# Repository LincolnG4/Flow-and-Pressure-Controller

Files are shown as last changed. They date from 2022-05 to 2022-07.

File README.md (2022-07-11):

# Protótipo de controle de fluxo de massa e leitura de pressão



O objetivo principal deste trabalho é desenvolver um protótipo de um sistema, composto de _hardware_, _firmware_ e _software_, para controle do fluxo e pressão de gases durante tratamento de materiais.

Os objetivos :

- Desenvolver um protótipo de um sistema de controle e alimentação de 4 _MFC_ MKS 500 _SCCM_ e leitura de pressão através de 1 Pirani APGX-M-NW16/ALI Edwards;

-  Desenvolver modos de funcionamento programados, tais como: liga/desliga de coleta sensores, pre-sets de gases comuns e alerta de erro;
- Desenvolver a placa de circuito impresso;
- Desenvolver a coleta de dados dos sensores.

## Wish list
Lista de desejos para o futuro do projeto:  
- [ ] Estudo mais detalhado dos resultados dos sinais aplicando metrologia; _`Em desenvolvimento`_
- [ ]  Sofware em Python para concatenar e gerar um grafico interativo; _`Em desenvolvimento`_
- [ ] Utilização de um hardware com Wi-Fi embutido e com mais de um núcleo, assim, permitindo multitarefas;
- [ ] Utilização de um processador de fácil integração na placa PCB;
- [ ] Otimização da programação; _`Em desenvolvimento`_
- [ ] Garantir a não utilização de um hardware genérico;
- [ ] Utilização de um roteador de internet dentro do laboratório;
- [ ] Remodelar o case para montagem por encaixe clicáveis ao invés de parafusos; _`Em desenvolvimento`_
- [ ] Função para alteração de data e hora do RTC; _`Em desenvolvimento`_

# 1. Visão Geral

 - Fonte de alimentação: 24 V ( **O módulo Step-Down aceita até 40 V de entrada, porém é necessário desmonta-lo e regular através do parafuso a saída para 7V** )
 - Sinal de saída: 0-5 V
 - Dimensões: 165,5 x 74,6 x 41 mm
 - Tela: Nextion Touch 320x240
 - Armazenamento: cartão microSD até 64 GB e 15GB em nuvem
 - Portas: 4 entradas DB9-macho, 1 entrada RJ45-femea e uma porta usb (debug)

## 1.1 Componentes

| Componente | Unidade | Preço/unidade (R$) | Total | Link | 
|--|--|--|--|--|
|Arduino Mega|1| 200,00 | 200,00  | [Compre](https://www.baudaeletronica.com.br/arduino-mega-2560-compativel-cabo-usb.html) |
| Capacitor 1uF |9| 0,23 | 2,07 | [Compre](https://www.eletrogate.com/capacitor-eletrolitico-1uf-x-50v ) |
| Conector DB9|4|3,00  | 12,00 |  [Compre](https://www.soldafria.com.br/conector-db9-macho-90-graus-solda-placa-p-1709.html) |
| Conector RJ45 |1|4,00 | 4,00  |  |
| Conector Alimentação|1| 2,50 | 2,50  | [Compre](https://www.robocore.net/conector/conector-dc-p4-femea)  |
| Fonte de alimentação 24V |1| 30,00 | 30,00 |  |
| Modulo Leitor de microSD | 1 | 12,00 | 12,00 | [Compre](https://www.eletrogate.com/modulo-micro-sd-card)  |
| Modulo LM2596 StepDown | 1 |15,00  | 15,00  | [Compre](https://www.filipeflop.com/produto/regulador-de-tensao-lm2596-conversor-dc-dc-step-down/) |
| Modulo WiFi ESP8266 |1| 20,00 | 20,00  | [Compre](https://www.eletrogate.com/modulo-wifi-serial-esp8266-esp-01) |
| Resistor 4.7k Ohms |6|0,05| 0,30 | [Compre](https://www.eletrogate.com/resistor-4k7-1-4w-10-unidades ) |
| Resistor 470 Ohms |8| 0,05 |0,40 |[Compre](https://www.eletrogate.com/resistor-4k7-1-4w-10-unidades )  |
| Resistor 220 Ohms |1| 0,05 | 0,05  |[Compre](https://www.eletrogate.com/resistor-4k7-1-4w-10-unidades ) |
| RTC 1302 | 1 | 10,00 |10,00 | [Compre](https://www.eletrogate.com/modulo-real-time-clock-ds1302) |
| Tela Nextion 320x240 |1| 120,00 |120,00  | [Compre](https://pt.aliexpress.com/item/32685352949.html?spm=a2g0o.productlist.0.0.10a12308w7t6Pf&algo_pvid=ee404ca7-f5a8-4c20-a123-40767543fb84&algo_exp_id=ee404ca7-f5a8-4c20-a123-40767543fb84-0&pdp_ext_f=%7B%22sku_id%22%3A%2260390805771%22%7D&pdp_npi=2%40dis%21BRL%21%21102.36%21%21%2133.26%21%21%402101d4a716547459631704164eff88%2160390805771%21sea)|
| Transistor BC337 |4| 0,27 | 1,08 | [Compre](https://www.eletrogate.com/ecfjb2rzm-transistor-npn-bc337)  |
| __TOTAL__ ||  |  __544,40__|  |

## 1.2 Tabela de fatores de correção dos gases

Faça o download da tabela de fatores de coreção dos gases em  [DOWNLOAD](https://github.com/LincolnG4/Flow-and-Pressure-Controller/blob/main/gasfactor.xlsx)

## 1.3 FAQ & Troubleshooting

> **A tela do produto está funcionando mas ele não retorna nenhum valor de medição**

- Certifique-se que os conectores da tela estão soldados corretamente 
- Conecte o Arduino na porta USB do seu computador e siga os passos  do tópico `3.3.1.1`
- Certifique-se que não aparecerá nenhuma mensagem de erro no monitor

# 2. Software Utilizados

| SOFTWARE        | DESCRIÇÃO|DOWNLOAD |
|----------------|-------------------------------|-------------------------------|
|`Cura3D`|Software para impressão 3D|https://ultimaker.com/software/ultimaker-cura|
|`FreeCAD 0.19`|CAD|https://www.freecadweb.org/downloads.php	|
|`Kicad 6.0`|Eletrônica e PCB |https://www.kicad.org/download/|
|`Nextion Editor`|Edição da interface LCD|https://nextion.tech/nextion-editor/|
|`Photopea`|Edição de fotos|https://photopea.com/|
|`Schematic editor`|Auto routing para trilha PCB|https://layouteditor.com/download|
|`Visual Studio Code e/ou Arduino IDE`|Edição de codigos|https://code.visualstudio.com / https://www.arduino.cc/en/software/download|

## 2.2 Links úteis 
[Basico do Arduino](https://www.if.ufrj.br/~gpenello/DisciplinasAntigas/Lab2_2018-1/GUIA_ARDUINO_v.2.pdf)
[Básico de Linguagem C++](https://www.inf.ufpr.br/ci208/NotasAula.pdf)
[Básico Cura 3D](https://3dlab.com.br/cura-3d-ultimaker/)
[FreeCAD -> SolidWorks / SolidWorks -> FreeCAD](https://forum.freecadweb.org/viewtopic.php?style=4&t=20778)

# 3. Passo a Passo de construção e instalação
## 3.1 Impressão do  case 3D

Faça o download dos arquivos para impressão 3D:
- [Gabinete](https://github.com/LincolnG4/Flow-and-Pressure-Controller/blob/main/Hardware/CAD/case_bottom-Body.stl)
- [Tampa](https://github.com/LincolnG4/Flow-and-Pressure-Controller/blob/main/Hardware/CAD/case_top-Body.stl)

Recomendações:

- Materiais: PLA ou ABS;
- Confira a [tabela de temperatura](https://3dlab.com.br/temperatura-na-impressao-3d/) para o bico para cada material;
- Configuração através do software [Cura 3D](#software-utilizados):  

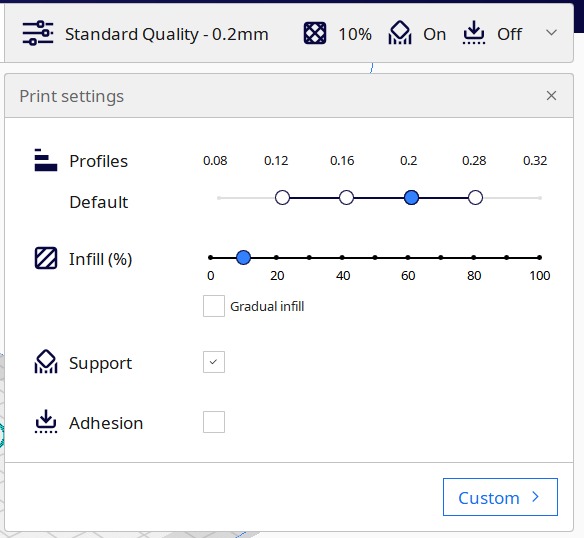
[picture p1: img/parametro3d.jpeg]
parameters


## 3.2 Configurando seu ambiente de programação
 Faça o download das bibliotecas a seguir e siga o passo a passo para configuração do seu ambiente de desenvolvimento.
 
### 3.2.1 Bibliotecas Externas Utilizadas 

#### Arduino 

Versão da placa: Arduino AVR Boards 1.8.3
| SOFTWARE        | DESCRIÇÃO|DOWNLOAD |
|----------------|-------------------------------|-------------------------------|
|`ITEADLIB Arduino`|Auxiliar no controle da tela LCD|https://github.com/itead/ITEADLIB_Arduino_Nextion|
|`ArduinoRTClibrary`|Controle do modulo RTC|https://github.com/chrisfryer78/ArduinoRTClibrary|
|`Timelib`|Manipulação time string|https://github.com/PaulStoffregen/Time|
|`UnixTime`|Manipulação de timestamp|https://github.com/GyverLibs/UnixTime|
_______

#### ESP01 

Versão da placa: esp8266 2.4.3
| SOFTWARE        | DESCRIÇÃO|DOWNLOAD |
|----------------|-------------------------------|-------------------------------|
|`WiFi Manager`|Auxiliar no controle do WiFi|https://github.com/tzapu/WiFiManager|

### 3.2.2 Como instalar uma biblioteca 

 1. Abra o link para o donwload da biblioteca (ex: `https://github.com/itead/ITEADLIB_Arduino_Nextion`) e faça o download do `.ZIP`  
download 
2. Abra o `Arduino IDE` e vá em `Sketch`>`Incluir biblioteca`> `Adicionar biblioteca .ZIP`  
include
3. Selecione a biblioteca que você fez o download no Passo 1 

### 3.2.3 Como instalar os gerenciador de placa 

#### Arduino 

1. Abra o `Arduino IDE` e clique em `Ferramentas`>`Placa`>`Gerenciador de placas`  

Como programar o NodeMCU com Arduino IDE   
2. Procure pela placa `Arduino AVR Boards` e selecione a versão `1.8.3`  
_______
#### ESP01
1.Abra o `Arduino IDE` e vá em `Arquivos`>`Preferências`  
2. No campo `URLs adicionais de Gerenciadores de Placas`, insira o link  `http://arduino.esp8266.com/stable/package_esp8266com_index.json`  

Como programar o NodeMCU com Arduino IDE
3. Vá em `Ferramentas`>`Placa`>`Gerenciador de placas`  
4. Procure pela placa `esp8266 by ESP8266 community` e selecione a versão `2.4.3`  
 
## 3.3  Implementando firmware
Com todas as bibliotecas configuradas, é possível desenvolver e carregar o código para o  Arduino, Esp e Nextion.

`Faça o download desse respositório e descompacte em alguma pasta do seu computado`:
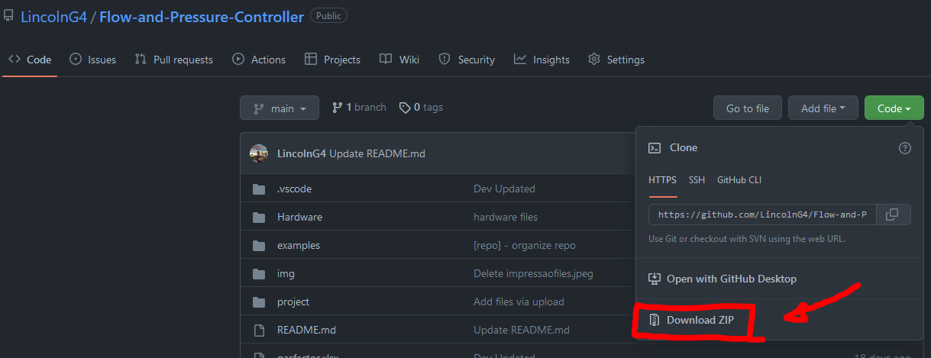
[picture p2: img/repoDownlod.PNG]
Download repositorio


### 3.3.1 Arduino
- Abra o [`Arduino IDE`](https://github.com/LincolnG4/Flow-and-Pressure-Controller/blob/main/README.md#2Software-Utilizados) em seu computador e vá em `Arquivo` > `Abrir`
- Vá até a pasta onde voce descompactou o repositório repositório, navegue por `Flow-and-Pressure-Controller-main` > `project` > `main.ino`   
- Certifique-se que a pasta `lib` esta na mesma pasta que o `main.lib`  
ConfMain
- Conecte o `Arduino Mega` via porta `USB`  
- Clique em `Ferramentas` e selecione as configurações :  
  
 *obs: a porta irá variar de acordo com a porta que o Arduino foi conectado ao seu dispositivo 

- Clique no botão `Verificar`, se o IDE não retornar nenhum erro, clique no botão `Carregar`
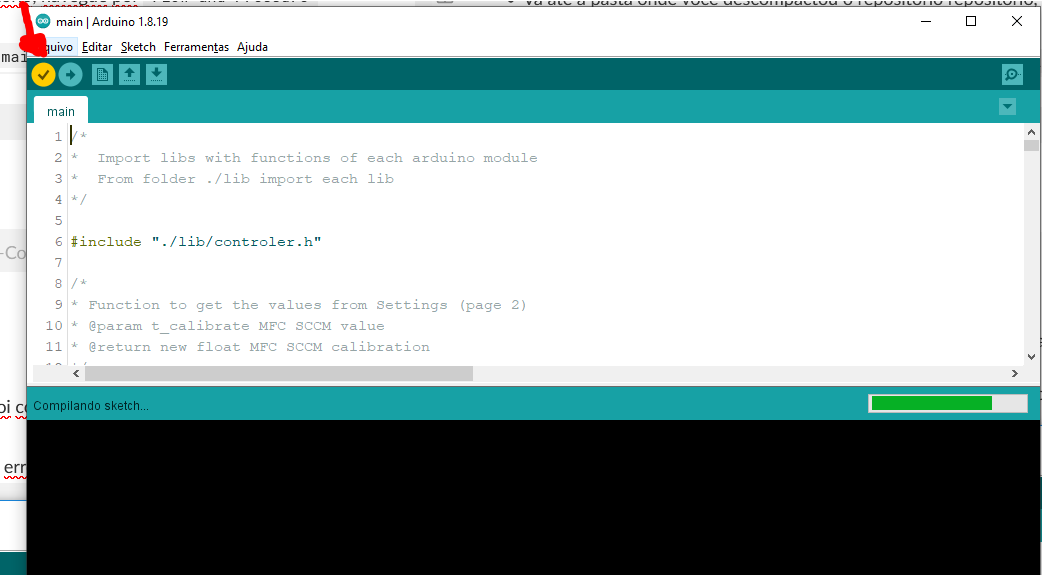
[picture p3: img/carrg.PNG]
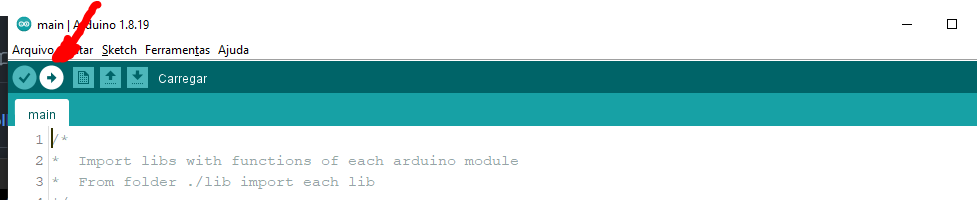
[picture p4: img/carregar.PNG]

- Se tudo ocorrer certo, o IDE ira retornar a mensagem `Carregado`

#### 3.3.1.1 Debugging Arduino
Caso você esteja desconfiado que o Arduino não está funcionando corretamente, ative a opção de debbuging:

1. Abra o `Arduino IDE` > `main.ino`
2. Pressione as teclas `Ctrl` + `F` para abrir o terminal `Localizar`
3. Preencha:

|**Campo** | **Valor** |
|--|--|
|_Localizar_ | `//Serial.` |
|_Substituir com_ | `Serial.` |

4. Clique em `Substituir todos`. Isso retira a marcação de comentário das mensagens serial de debug, ou seja, após as substituições as mensagens de rotina do arduino serão mostradas via USB

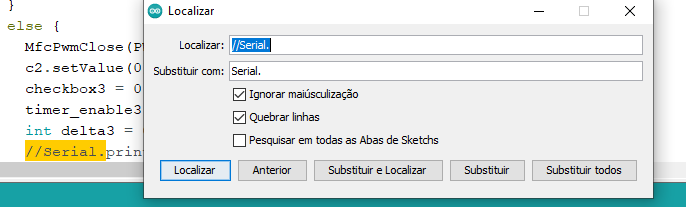
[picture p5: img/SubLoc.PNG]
Localizar e substituir
  
5. Carregue o código, ao fim do carregamento, desconecte o USB e conecte novamente.
6. Clique em `Ferramentas` > `Monitor Serial`
7. Agora todas as atividades do Arduino serão mostradas no monitor.

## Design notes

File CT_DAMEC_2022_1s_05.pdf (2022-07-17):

UNIVERSIDADE TECNOLÓGICA FEDERAL DO PARANÁ

GABRIEL ESPINOLA LINCOLN FERREIRA DOS SANTOS

DESENVOLVIMENTO DE UM PROTÓTIPO PARA CONTROLE DE FLUXO DE

MASSA E LEITURA DE PRESSÃO DE GASES DURANTE O TRATAMENTO

TÉRMICO DE MATERIAIS

CURITIBA

2022

4.0 Internacional (https://creativecommons.org/licenses/by-nc-nd/4.0/deed.pt_BR)

Esta licença permite download e compartilhamento do trabalho desde que sejam atribuídos créditos ao(s) autor(es), sem a possibilidade de alterálo ou utilizálo para fins comerciais. Conteúdos elaborados por terceiros, citados e referenciados nesta obra não são cobertos pela licença.

GABRIEL ESPINOLA LINCOLN FERREIRA DOS SANTOS

DESENVOLVIMENTO DE UM PROTÓTIPO PARA CONTROLE DE FLUXO DE

MASSA E LEITURA DE PRESSÃO DE GASES DURANTE O TRATAMENTO

TÉRMICO DE MATERIAIS

Design of a prototype for mass flow control and gas pressure reading during

the heat treatment of materials

Trabalho de Conclusão de Curso apresentado como requisito à obtenção do título de Bacharel em Engenharia Mecânica da Universidade Tecnológica Federal do Paraná (UTFPR).

Orientador(a): Prof. Dr. Márcio Mafra
Coorientador(a): | Prof. | Dr. | Euclides | Alexandre
Bernardelli.

CURITIBA

2022

GABRIEL ESPINOLA LINCOLN FERREIRA DOS SANTOS

DESENVOLVIMENTO DE UM PROTÓTIPO PARA CONTROLE DE FLUXO DE

MASSA E LEITURA DE PRESSÃO DE GASES DURANTE O TRATAMENTO

TÉRMICO DE MATERIAIS

Trabalho de Conclusão de Curso de Graduação apresentado como requisito para obtenção do título de Bacharel em Engenharia Mecânica da Universidade Tecnológica Federal do Paraná (UTFPR).

Data de aprovação: 14/junho/2022

___________________________________________________________________________ Márcio Mafra
Doutorado em Ciência e Engenharia dos Materiais Universidade Tecnológica Federal do Paraná

___________________________________________________________________________ Euclides Alexandre Bernardelli Doutorado em Ciência e Engenharia dos Materiais Universidade Tecnológica Federal do Paraná

___________________________________________________________________________ Sidney Carlos Gasoto
Mestre em Engenharia de Produção e Sistemas Universidade Tecnológica Federal do Paraná

___________________________________________________________________________ Walter Luís Mikos
Doutorado em Engenharia Mecânica Universidade Tecnológica Federal do Paraná

CURITIBA

2022

Dedico este trabalho à minha família, amigos e professores que me auxiliaram nessa trajetória.

RESUMO

A engenharia de superfícies e tratamento de materiais tem uma crescente demanda por processos que garantam componentes com alterações significativas nas propriedades mecânicas, térmicas e químicas. Esses processos exigem controle constante dos parâmetros de fluxo de massa e pressão dos gases presentes no sistema. Este trabalho tem como objetivo desenvolver um protótipo para controle de sistemas com controladores de fluxo de massa de gases MKS 500 SCCM e leitura de sensores de pressão Pirani APGX-M-NW16/ALI Edwards que se adapta aos gases utilizados e as calibrações dos sensores. Além disso, forneça um método de armazenamento dos dados de medição dos sensores, offline e online. Sendo o método online, através das plataformas Google Sheets e Grafana e os método offline através do cartão microSD. O equipamento é manipulado via uma tela sensível ao toque onde o usuário pode configurar os sensores utilizados. O projeto aplica metodologias de desenvolvimento de produtos, tratamento de materiais, eletrônica, processamento de sinais e programação.

Palavraschave: controle de fluxo de massa; leitura de pressão; tratamento de materiais; pirani.

ABSTRACT

There is a growing demand for processes of materials science, that can induce engineering materials to alter their mechanical, thermal, and chemical properties. These processes require constant parameter's control of the mass flow and pressure of the gases in the system. This project aims to develop a prototype to control systems with mass flow controllers MKS 500 SCCM and Pirani APGX-M-NW16/ALI Edwards pressure sensor reading. Also, it stores the measurement data from sensors by offline and online protocol. The online method is by Google Sheets and Grafana platforms and the offline method is through the microSD card. The equipment is manipulated by a touch screen where the user can configure the sensors. The research project surveys methodologies for product development, material handling, electronics, signal processing and programming.

Keywords: mass flow control; pressure reading; treatment of materials; pirani.

LISTA DE ILUSTRAÇÕES

Figura 2 Diagrama esquemático do reator de plasma de baixa pressão .........15

Figura 9 Pressão medida sobre por pressão real para diferentes gases ........21

Figura 16 Diagrama redução de ruídos por passabaixa (a) entrada de sinal

Figura 28 – Esquemático simplificado do sistema de tratamento de superfície

Figura 31 – Análise de erro ADC1 (GPIO36) para 11 dB (0 – 3900 mV) e Wi-Fi

Figure 45 – Tampa CAD | 51
Figura 46 – Posicionamento e configuração Cura 3D | 51
Figura 47 Parâmetros de impressão | 52
Figura 48 – Montagem do protótipo | 52
Figura 49 – Diagrama de sequência | 53
Figura 50 Diagrama de coleta de dados | 54
Figura 51- Mapa da interface gráfica | 54
Figura 52 – Menu de configurações “Settings” | 55
Figura 53 – Menu de gases cadastrados | 55
Figura 54 – Menu de controle dos sensores “Free Mode” | 56
Figura 55 Estrutura dos arquivos | 57
Figura 56 Transformação de tensão para pressão | 61
Figura 57 Esquema de abertura e fechamento | 63
Figura 58 Servidor web gerenciador de WiFi | 64
Figura 59 Panilha recebendo dados do ESP01 | 66
Figura 60 Apps Scripts | 66
Figura 61 Dashboard no Grafana | 68
Figura 62 Consulta planilha | 68
Figura 63 Modelos de gráfico | 69
Figura 64 – Especificações multímetro para tensão contínua | 70
Figura 65 – Preparação do laboratório para realização do teste | 70
Figura 66 Leitura da pressão no reator com fluxo constante de hidrogênio à
250 SCCM durante 50 segundos | 71
Figura 67 – Leitura de pressão no reator com fluxo constante de hidrogenio à
250 SCCM durante 35 segundos | 71
Figura 68 – Precisão da medição do Pirani | 72
Figura 69 Função contínua variação de abertura de válvula | 73
Figura 70 Resultados individuais da função contínua | 72
Figura 71 Função pulsada 165 segundos | 74
Figura 72 Dashboard Grafana | 74
Figura 73 Taxa de aquisição x Número de MFC’s aquisitando | 76
Código 1 Função "MFCPwnON" | 57
Código 2 Função "MFCPwmClose" | 58
Código 3 Função "MFCRead" | 58
Código 4 Função "PiraniRead" | 59
Código 5 Função "piraniUpdateScreen" | 61
Código 6 Modo contínua | 62
Código 7 Modo pulsado | 63
Código 8 Função enviar para a API | 65
Código 9 Google Sheets API | 66
Quadro 1 Benchmarking de controladores | 22
Quadro 2– Comparação Arduino Mega x ESP32 | 40
Quadro 3 – Pinagem RJ45 Pirani Edwards | 42
Quadro 4 – Sensores Pirani compatíveis | 43
Quadro 5 Pinagem MFC DB9 | 43
Quadro 6 – Compatibilidade de MFC | 44

LISTA DE ABREVIATURAS E SIGLAS

3D | Tridimensional
ASP | Analog Signal Processor
CSV | Commaseparated values
GUI | Graphical user interface
IDE | Integrated Development Environment
IoT | Internet of things
MFC | Mass Flow Controller
NoSQL | Not Only Structured Query Language
PCB | Printed circuit board
PWM | Pulse Width Modulation
RTC | Realtime clock
SCCM | Standard Cubic Centimeters Per Minute
SLM | Standard Liter Per Minute
SPI | Serial Peripheral Interface
SQL | Structured Query Language
TCC | Trabalho de conclusão de curso
UTFPR | Universidade Tecnológica Federal do Paraná

LISTA DE SÍMBOLOS

A | Ampere
Hz | Hertz
V | Volts
Ω | Ohms
kb | Kilobit
Mbps | Megabit por segundos

SUMÁRIO

1 INTRODUÇÃO

A crescente demanda por componentes com alterações significativas nas

propriedades mecânicas, térmicas e químicas, como mais resistência ao desgaste e

corrosão, faz com que empresas e pesquisadores busquem novas formas de suprir

essas necessidades. Tradicionalmente, buscase o desenvolvimento de novas ligas

como forma de solução. Porém, o desenvolvimento de novas ligas exige custo e

tempo, que muitas vezes se torna o fator decisivo para não prosseguir com as

pesquisas. Logo, a engenharia de superfícies e materiais vêm para suprir esses

requisitos de alteração nas propriedades tribológicas e triboquímicas (PINEDO, 2004).

A nitretação é um exemplo de processo que visa a melhoria das propriedades

de superfície (Figura 1). O tratamento consiste em submeter o material a um ambiente

de baixa pressão na presença de uma mistura gasosa contendo nitrogênio (HULTMAN, 2001). É aplicada uma diferença de potencial, através de dois eletrodos,

para ionizar a mistura e o substrato é posicionado dentro de uma câmara de vácuo

junto ao eletrodo de potencial negativo. Ocorre o aceleramento de íons da atmosfera

controlada que colidem contra o substrato, promovendo pulverização e aquecimento,

o aumento de temperatura associado a presença de espécies nitretantes favorecem

a modificação superficial do material ocasionando a alteração da dureza superficial,

resistência mecânica, fadiga e outros (XI, 2007).

Figura 1 Nitretação a plasma em peça

Fonte: Autor (2018)¹

Historicamente, o processo de nitretação a plasma foi desenvolvido por

Berghaus no início do século XX. Porém, devido às restrições tecnológicas da época,

Ilustrações e Tabelas sem indicação de fonte são de autoria própria o processo não atingia os parâmetros fluxo de massa e de pressão dos gases exigidos

para o sistema. Assim, essa tecnologia apenas teve pleno desenvolvimento no fim do

século XX, possibilitado pelos avanços tecnológicos, principalmente relacionados à

eletrônica e automação (PINEDO, 2004).

A Figura 2 apresenta um exemplo de como a tecnologia está presente para o

funcionamento desse processo. O esquemático representa um sistema de reator a

plasma de baixa pressão, no qual a amostra (sample) é posicionada entre os eletrodos

e a saída de gás (gas shower). O sistema de entrada de gás permite a mistura dos

gases controlado através do controlador de fluxo de massa (Mass flow controller) ou

MFC. A câmara é esvaziada pela bomba a vácuo. A pressão na câmara é medida

através do sensor Pirani. Um controlador é usado para alimentar o Pirani e os MFC

(PANDIYARAJ, 2014).

Figura 2 Diagrama esquemático do reator de plasma de baixa pressão

Fonte: Pandiyaraj (2014)

A Figura 3 apresenta um controlador de fluxo de massa (MFC) que permite a

introdução precisa de frações volumétricas diversas dos gases -H2, N2, Ar e O2- de

modo a compor uma atmosfera gasosa controlada para cada material, sendo crucial

para atingir os resultados desejados (HELMERSSON, 2006).

Figura 3 Controlador de fluxo de massa

Fonte: MKS Instruments (2021)

Juntamente com o MFC, esse processo necessita de controle de pressão que

é, geralmente, realizado em níveis de vácuo que variam entre 1 Torr e 10 Torr

(133,322 Pa e 1.333,22 Pa). Essa pressão pode ser monitorada através de um sensor

Pirani, apresentado na Figura 4. (TOPALLI, 2009). Segundo Alves (2001), a pressão

de trabalho está diretamente relacionada com as colisões elétronsíonsátomos,

sendo um fator determinante para a realização de tratamentos de nitretação a plasma.

Figura 4 Sensor Pirani

Fonte: Edwards Vacuum (2021)

O controlador de alimentação, Figura 5, é um hardware que funciona como

fonte de alimentação, leitura das medições e ajuste das válvulas dos MFC’s

conectados. Logo, o sistema visa facilitar o ajuste de abertura da válvula dos

equipamentos, a qual é determinado pela magnitude do sinal emitido pelo controlador

para o MFC. Além de monitorar os valores medidos por cada equipamento conectado

a ele (DILLON, 2001).

Figura 5– Controlador de alimentação 247D

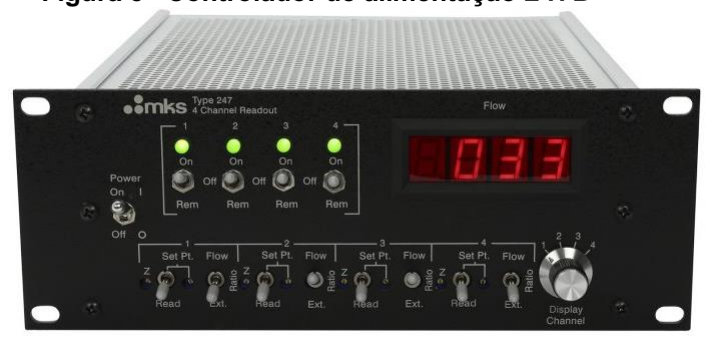
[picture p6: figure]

Fonte: MKS Instruments (2021)

Pretendese nesse projeto desenvolver um protótipo de controlador de

alimentação e leitor de módulos MFC/Pirani, visando ser uma alternativa nacional do

equipamento.

1.1 Caracterização do problema e justificativa

O controlador de alimentação é essencial para gerenciar o funcionamento dos

módulos durante o processo de tratamento de superfícies. A necessidade de

monitorar e controlar o fluxo e a pressão é de plena importância durante o tratamento

de superfícies por gases. Os erros podem trazer resultados completamente diferentes

do esperado. Portanto, o presente trabalho identifica a oportunidade de minimizar a

interferência humana nesse processo e, assim, automatizar os sensores para melhor

performance através de um microcontrolador.

Além disso, atualmente, apenas 2 empresas internacionais -MKS instruments

e Brooks instruments produzem equipamentos como esse que apenas dão suporte

para módulos da mesma marca. Esses controladores têm custo elevado, podendo chegar até R$ 57.000,00. A falta de uma tecnologia nacional faz surgir a oportunidade

de desenvolvimento desse sistema com um custo mais acessível.

1.2 Objetivos

O objetivo principal deste trabalho é desenvolver um protótipo de um sistema,

composto de hardware, firmware e software, para controle do fluxo de massa dos

gases e monitoramento da pressão de gases durante tratamento de materiais.

Os objetivos específicos que devem ser cumpridos para que seja possível

alcançar o objetivo geral são:

- Desenvolver um protótipo de um sistema de controle e alimentação de 4

MFC MKS 500 SCCM e leitura de pressão através de 1 Pirani APGX-M-NW16/ALI

Edwards;

- Desenvolver modos de funcionamento programados, tais como: liga/desliga

de medição dos sensores, presets de gases comuns e alerta de erro;

- Desenvolver a placa de circuito impresso;
- Desenvolver a coleta de dados dos sensores que tenham resultados do erro

de medição e precisão melhor ou equivalente ao multímetro atualmente utilizado no

laboratório.

2 REFERENCIAL TEÓRICO

Esta seção apresenta os conceitos teóricos necessários para o

desenvolvimento do trabalho.

2.1 Controladores de fluxo de massa

O controlador de fluxo de massa controla automaticamente a taxa de fluxo de

um gás de acordo com o set point enviado por um sinal elétrico sem ser afetado pelas

condições de ou mudanças na pressão do gás (HORIBA, 2021). O MFC pode receber

um set point de 0 a 100% de escala, mas normalmente é operado em 10% a 90%,

onde a melhor precisão é alcançada. O dispositivo controlará a taxa de fluxo até o set

point fornecido (CHOI, 2013).

Conforme a Figura 6, a seção onde ocorre a medição de taxa de fluxo inclui

um sensor, desvio, válvula de controle de taxa de fluxo e circuitos especiais. O gás é

alimentado através do inlet e parte do gás flui para o sensor, o qual mede a taxa de

fluxo, e outra para a válvula, a qual modifica a taxa de fluxo de modo que a diferença

entre a taxa de fluxo medida e a taxa de fluxo recebida do sinal de set point seja zero

(HORIBA, 2021).

Figura 6 Estrutura interna MFC

Fonte: Adaptado de Horiba (2013)

O sensor de taxa de fluxo, Figura 7, consiste em um tubo de pequeno diâmetro

usado para desviar uma pequena quantidade de gás do fluxo principal. Um aquecedor

é instalado entre um par de termômetros. A taxa de fluxo de massa é medida por meio

de fenômenos de transferência de calor entre um aquecedor e o gás fluindo dentro do

tubo (TISON, 1996).

Figura 7 Sensor de taxa de fluxo

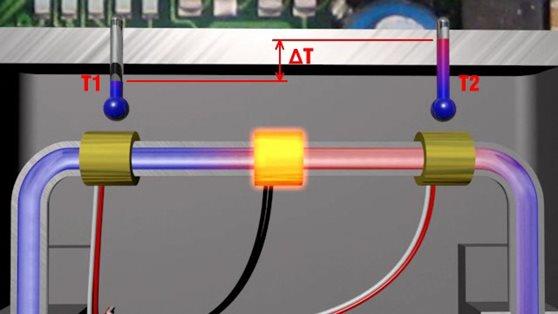
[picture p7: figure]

Fonte: Bronkhorst (2021)

2.2 Pirani

O sensor Pirani de vácuo, Figura 8, consiste em um filamento de metal,

usualmente de platina, suspenso em um tubo em qual é conectado ao sistema de

vácuo. O filamento é conectado a um circuito elétrico que permite a leitura da pressão

após a calibração (LAMMERINK, 2001).

Figura 8 Estrutura sensor pirani

Fonte: Adaptado de Sens4 (2021)

O medidor Pirani mede a condutividade térmica do fio aquecido. Essa

condutividade corresponde diretamente a pressão do vácuo para o gás circundante o

qual dissipa o calor para a parede do tubo. Na faixa de fluxo molecular, a transferência

térmica é proporcional à densidade do número molecular e, portanto, à pressão. Em

alta pressão, a alta densidade do gás e o curto caminho livre médio entre as moléculas

resultarão em alta condutividade térmica (LAMMERINK, 2001).

Segundo Martini (2012), o filamento do sensor Pirani é operado em uma ponte

de Wheatstone como um dos quatro braços da ponte. Como apresentado na Figura

9, as leituras do medidor devem ser corrigidas ou calibradas para diferentes gases.

Sendo as curvas definidas pelas taxas de transferência de calor para as moléculas de

cada gás.

Figura 9 Pressão medida sobre por pressão real para diferentes gases

Fonte: Adaptado de Bishop (2015)

Considerando o gráfico apresentado por Bishop (2015), se a temperatura do

filamento, que é encontrada na resistência, é mantida constante, sua produção de

calor será função da pressão. Porém, não é linear, pois a radiação térmica também

influenciará na saída de calor. A taxa de perda total de energia WT é dada por:

WT = WR + WG | (2.1)

É possível examinar as funções de dependência de cada termo. Sendo dl o

comprimento ao longo de um fio de diâmetro D1, emissividade ԑ1, e temperatura T1

localizado ao longo do cilindro de raio r2, emissividade ԑ2, temperatura da vizinhança

T2 e σ a constante de Stefan-Boltzmann. Assumindo r2 ≫ D1 e T1 > T2, a taxa de

transferência de calor é dado por:
WR = ԑ1σ (T1

4 − T2

4
)2πD1 dl | (2.2)

Logo, o material ideal para o filamento do sensor apresenta uma emissividade

baixa e estável, explicando a recorrência do uso de platina para o projeto desses

equipamentos. Assim, fazendo o mesmo para a taxa de transferência de calor para as

moléculas de gás, temos:

WG =

1(γ + 1)
4(γ − 1)

α√
2k
πmT2

(T1 − T2

)p

| (2.3)

Onde γ = Cp/Cv é a proporção de calores específicos do gás, m é a massa de

uma molécula de gás e k é a constante de Boltzmann. Logo, como mencionado acima,

com a equação WG é possível definir cada curva da Figura 8 para os múltiplos gases

(MARTINI, 2012).

2.3 Controladores de alimentação e leitura

O controlador de alimentação e leitura é projetado como fonte de alimentação

e leitura de sinal, gerador de sinal de set point para controladores de fluxo de massa

analógicos (MFC’s). Em geral, é um instrumento versátil que pode ser usado

separadamente ou como parte de um sistema de controle maior (MKS, 2021).

2.3.1 Benchmarking

O benchmarking dos controladores de alimentação e leitura similares ao

desenvolvido neste trabalho é uma etapa crucial no desenvolvimento do sistema.

Através desse, é possível entender e comparar as opções presentes no mercado.

Entendendo quais são os pontos fortes e mínimos para o desenvolvimento de uma

solução competitiva.

O Quadro 1 compara os 2 principais produtos presente no mercado para

venda. Ambos são comercializados internacionalmente e revendidos no Brasil por

empresas autorizadas.

Quadro 1 Benchmarking de controladores

Empresa | MKS Instruments | Brook Instrument
Modelo | 247 | 254
Dimensões (mm) | 240,5x274,3x88,1 | 211x113x58.8
Alimentação | 100 - 120 Vac | 12-24 Vdc ou 100 - 240 Vac
Material case | Aluminio | ABS Cycolac
Número de canais | 4 | 4
Tela | LED 1 linha x digito 3 1/2 0.56" | LCD 8 linhas x 40 digito
Output de sinal | 0-5 volts | 0-5 volts
Compatibilidade | Modulo de controle massa (apenas MKS Intruments) | Modulo de controle pressao e massa (apenas Brook Intruments)
Armazenamento de dados | Não armazena os dados | "100 anos de rentenção"
Funções | Alimentação, leitura e controle de set point | Alimentação, leitura, controle de set point e armazenamento das medicoes
Orçamento | R$ 21.395,00 | R$ 57.634,50
Revendedor/data Orçamento | Ohmini 21/10/2021 | Contech 20/10/2021

2.3.2 MKS modelo 247

Analisando os dados coletados no Benchmarking, ambos os controladores são

de pequeno porte, comportam até 4 módulos e set point de até 5 V baseado no fluxo

da medição. Para o equipamento da MKS 247, Figura 10, temos:

Figura 10 – Controlador de alimentação MKS

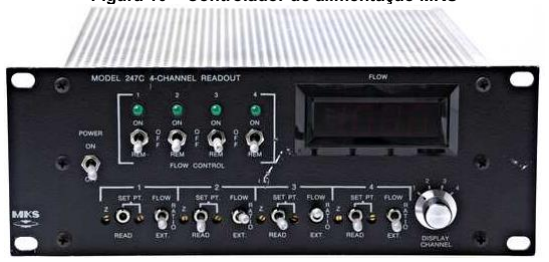
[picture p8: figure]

Fonte: MKS Instruments (2021)

Pontos positivos

- Preço mais barato comparado ao seu concorrente.

Pontos negativos

- Não armazena e não apresenta nenhuma forma de coletar os dados

medidos;

- Tela pequena, apresenta um dado por vez;
- 1 entrada DB9 para o MFC e 1 entrada DB25;
- Compatibilidade apenas com módulos da MKS;
- Apenas compatibilidade com módulos de controle de massa.

Como apresenta a Figura 11, o controle do equipamento da MKS é realizado

manualmente. O controlador contém 4 potenciômetros manuais para ajuste do set

point (0-5 V) e uma interface digital (Digital Panel Meter).

Figura 11 Painel de controle frontal

Fonte: Adaptado de MKS Instruments (2021)

O painel de controle traseiro, apresentado na Figura 12, há apenas 1 entrada

DB9 para o MFC e 1 entrada DB25. Além disso, o controlador contém 4 portas DB15.

Os quatro potenciômetros de 10 voltas são usados para inserir o fator de escala, que

reduz o sinal de saída do transdutor +5 V para que o medidor de painel digital exiba a

taxa de fluxo e o ponto de ajuste diretamente em sccm (Standard Cubic Centimeters

Per Minute) ou slm (Standard Liter Per Minute) .

Figura 12 Painel de controle traseiro

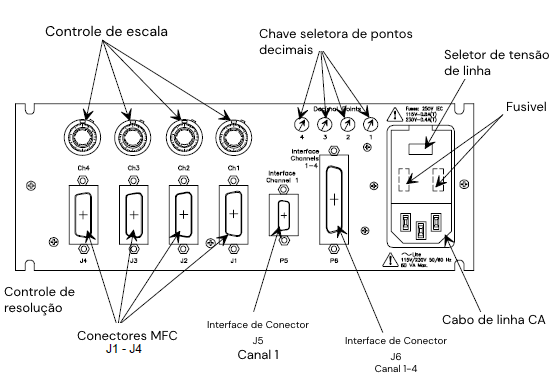
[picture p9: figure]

Fonte: Adaptado de MKS Instruments (2021)

2.3.3 Brooks modelo 254

Para o equipamento da Brooks Instrument, Figura 13, temos:

Figura 13 – Controlador de alimentação Brooks Instrument

Fonte: Brooks Instruments (2021)

Pontos positivos

- Portabilidade;
- Tela com exibição dos 4 módulos ao mesmo tempo;
- Armazenamento interno das medições;
- Compatibilidade com módulos de controle de massa e pressão;
- Coleta externa dos dados.

Pontos negativos

- Preço alto;
- Compatibilidade apenas com módulos Brooks Instrument;
- Compatibilidade apenas para módulo com entrada DB15.

Como apresentado na Figura 14, o equipamento da Brooks é portátil e tem

ajuste para uso em diversas posições. O controle do equipamento é digital. A parte

frontal contém a tela para leitura das medições e os botões para controle de sensor e

set point.

Figura 14 Vista frontal controlador Brooks Instrument

Fonte: Adaptado de Brooks Instruments (2021)

A vista traseira do controlador, Figura 15, apresenta 4 entradas para módulos

com conexão via DB15. A alimentação é feita por um conector DB9. O equipamento

permite extrair os dados das medições através de uma comunicação serial.

Figura 15 Vista traseira controlador Brooks Instrument

Fonte: Adaptado de Brooks Instruments (2021)

2.4 Processamento de sinal analógico

O processamento de sinal analógico (ASP) é qualquer processamento de

sinal conduzido por circuitos analógicos cujo valores são normalmente representados

como tensão, corrente elétrica ou carga elétrica em torno dos dispositivos eletrônicos.

Um erro ou ruído afetando tais quantidades físicas resultará em um erro

correspondente nos sinais representados (EL-SABA, 2015). Podese citar como

exemplo o filtro analógico elétrico é um exemplo de processamento do sinal, no qual

é usado para passar certos comprimentos de onda, ou frequências, e atenuar ou

bloquear. (PAARMANN, 2001).

2.4.1.1Filtro passabaixa

O objetivo do filtro passabaixa é reduzir a amplitude dos componentes

indesejados do sinal, dos quais o primeiro a ser considerado é o ruído. A Figura 16

ilustra a maneira como o filtro passabaixa reduz esse ruído (WILMSHURST, 1990).

Figura 16 Diagrama redução de ruídos por passabaixa (a) entrada de sinal vin, (b) processo de média, (c) saída filtrada vo

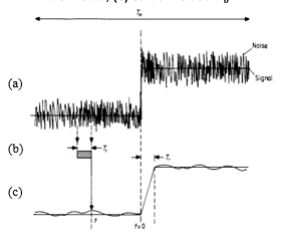
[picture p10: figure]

Fonte: Wilmshurst (1990)

Na Figura 15 (a) apresenta a entrada de um sinal vin com ruído. O efeito do

filtro é produzir a tensão de saída vo com ruído reduzido, subsequente da "média

contínua" (b), ao longo da tensão de entrada (a). No tempo t, vo é a média de vin, ao

longo do período mostrado de t − Tr até t. No qual, Tr é o tempo finito para o sinal de

saída vo realizar a média. Logo, Tr é o tempo de resposta do filtro. Em termos

matemáticos, segundo demonstrado por Wilmshurst (1990), a equação (2.4)

representa o sinal de saída vo.

vo(t) = Tt

−1 ∫ vin(t
′
) dt′

t

t−Tr

(2.4)

Eletronicamente, o filtro passabaixa simples consiste em um resistor em série

com um capacitor em paralelo com a carga, como apresenta a Figura 17.

Figura 17 Filtro passabaixa RC

Fonte: Wilmshurst (1990)

O capacitor exibe oposição a corrente alternada e bloqueia os sinais de alta

frequência, fazendo com que eles passem pela carga (WILMSHURST, 1990). A

frequência de corte é determinada pela escolha da resistência (R) e da capacitância

(C):

fc =

1
2πRC

(2.5)

Logo, um exemplo de curva de resposta de frequência para o filtro de passa-

baixa é apresentado na Figura 18. Em geral, é padronizado um valor de 3 dB para a

frequência de corte (WILMSHURST, 1990).

Figura 18 Curva de resposta de frequência para filtro passabaixas

Fonte: Adaptado de Qazizadeh (2017)

2.5 Microcontrolador

Um microcontrolador é um circuito integrado projetado para realizar uma

atividade específica em um sistema embarcado. O processador central do

microcontrolador interpreta os dados que recebe de seus periféricos de entrada/saída

para realizar a atividade para qual foi programado (KOUTROULIS, 2001).

2.5.1 Arduino

O Arduino, representado na Figura 19, é uma plataforma de prototipagem

eletrônica opensource que se baseia em hardware e software flexíveis. O hardware

é um microcontrolador, em geral, baseado em um processador ATmega. Possui pinos

de entrada/saída analógicos e digitas, dos quais podem ser utilizados como saídas de

PWM (Pulse Width Modulation). A utilização do Arduino como produtos/protótipos de

IoT, wearables e impressoras 3D é bastante comum. Com uma gama de modelos e

especificações (ARDUINO, 2021).

Figura 19 Arduino mega

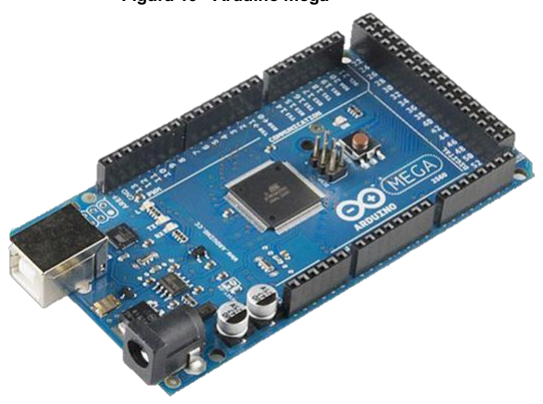
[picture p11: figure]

Fonte: Arduino (2021)

O software Arduino é publicado como código aberto. A linguagem de

programação é C ++, tendo a possibilidade de ser programado por AVR C linguagem

na qual a placa se baseia. (ARDUINO, 2021).

2.5.2 ESP01

O ESP é um microchip de baixo custo produzido pela Espressif Systems que

desempenha a função de um microcontrolador. A Figura 20 apresenta um ESP8266,

modelo com um processador L106 de 32bits, memória flash embutida de 1 MiB,

módulo Wi-Fi e programar funções especificais com conexão TCP/IP (ESPRESSIF,

2021).

Figura 20 ESP8266

Fonte: Espressif (2021)

A sua linguagem de programação mais popular é C++, possibilitando ser

utilizado a IDE (Integrated Development Environment) do Arduino, utilizando a

comunicação via cabo microusb (ESPRESSIF, 2021).

2.5.3 ESP32

O ESP32, Figura 21, é um microcontrolador com conectividade Wi-Fi e

Bluetooth integrada para uma ampla gama de aplicações. Com 4 MB de memória

flash, o ESP32 permite criar variadas aplicações para projetos de IoT, acesso remoto,

webservers e dataloggers, entre outros. O ESP32 é criado e desenvolvido pela

Espressif Systems, uma empresa chinesa com sede em Xangai (ESPRESSIF, 2021).

Figura 21 – ESP32

Fonte: Espressif (2021)

A sua linguagem de programação mais popular é C++, possibilitando ser

utilizado a IDE (Integrated Development Environment) do Arduino, utilizando a

comunicação via cabo microusb (ESPRESSIF, 2021).

2.6 Internet das coisas (IoT)

A internet das coisas (IoT) descreve a rede de objetos físicos – coisas – que

estão embarcados com sensores, softwares e outras tecnologias com o intuito de

conectar e trocar dados com outros dispositivos e sistemas pela internet. Esses

objetos variam entre objetos domésticos comuns a ferramentas industriais sofisticadas

(ABDUL-QAWAY, 2015).

2.7 Armazenamento de dados

A confiabilidade dos dados é crucial nos sistemas embarcados. Referindose

a confiabilidade como a capacidade do sistema garantir a integridade e efetividade

dos dados mesmo se o sistema sofrer algum dano, como falha de memória, erro

humano ou falta de alimentação (CHAO, 2012).

Existem várias formas de armazenar dados, as principais são pela sua

estrutura ou pelo tipo de arquivo (texto, imagem, número) que alocam. Os mais

comuns para coleta de dados de sensores são: relacional, não relacional e dados

separados por vírgula (ORACLE, 2021).

2.7.1 Banco de dados relacional (SQL)

O banco de dados relacional é organizado em tabelas. Os dados têm um

relacionamento predefinido entre si em cada tabela. Cada tabela é organizada por

colunas e linhas (ORACLE, 2021). As tabelas são usadas para reter a informação

sobre os objetos a serem representados no banco de dados. Como apresentado na

Figura 22, as linhas na tabela representam uma coleção de valores relacionados de

um objeto. (PEREIRA, 2009).

Figura 22 Esquema banco de dados relacional

Fonte: Oracle (2021)

2.7.2 Banco de dados não relacional (NoSQL)

O banco de dados não relacional é um banco de dados de código aberto que

não possui um esquema de tabelas de linhas e colunas. Como apresentado na Figura

23, ele utiliza um modelo otimizado e escalável para requisitos específicos de dados

que serão armazenados, como documentos, orientação para coluna, orientação por

gráficos e outros (PLECHAWSKA-WOJCIK, 2017). Logo, a especificidade e

escalabilidade contribuem com sua flexibilidade e possibilitando desafios típicos de

big data, variedade e velocidade de armazenamento (MICROSOFT, 2021).

Figura 23 Esquema de banco de dados não relacional

Fonte: Microsoft (2021)

2.7.3 Valores separados por vírgula (CSV)

O formato mais simples e amplo para armazenamento de um conjunto de

dados, predominantemente tabulares, é os valores separados por vírgula (CSV). Cada

registro está em uma linha e os campos de dados indicados são separados por uma

vírgula (AHMED, 2017).

Como apresentado na Figura 24, segundo Carvalho (2015), a recomendação

geral é seguir a definição para CSV estabelecida pela Internet Engineering Task

Force:

- Os registros estão localizados em linha separadas delimitada por uma

quebra de linha;

- O último registro do arquivo não pode ter quebra de linha final;
- Uma linha de cabeçalho opcional pode existir na primeira linha do

arquivo;

- Os campos que contêm quebras de linha, aspas duplas e vírgulas devem

ser colocados entre aspas duplas;

Figura 24 Esquema armazenamento de valores separados por vírgula

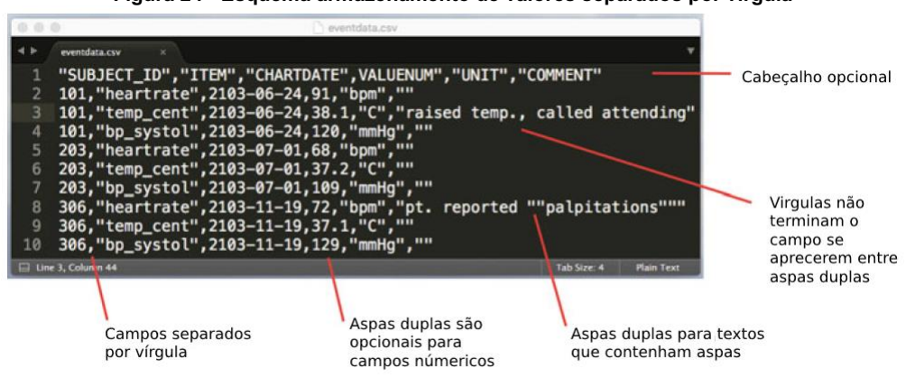
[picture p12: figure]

Fonte: Adaptado de Pollard (2016)

3 PROCEDIMENTOS METODOLÓGICOS

3.1 Metodologia de projeto

A metodologia DevOps foi utilizada neste trabalho. O seu objetivo é encurtar

o ciclo de vida de desenvolvimento de sistemas e fornecer entrega contínua com

qualidade. O DevOps permite que funções anteriormente isoladas atuem de forma

coordenada e colaborativa para produzirem produtos melhores e mais confiáveis

(MICROSOFT, 2021). O ciclo de vida do DevOps consiste em oito fases (Figura 25):

Figura 25 Ciclo desenvolvimento DevOps

Fonte: Adaptado de Microsoft (2021)

1. Planejar: elaboração de um plano prévio antes dos desenvolvedores

começarem a programar. Requisitos e feedbacks são coletados das partes

interessadas. No caso deste trabalho, foram coletados feedbacks dos professores que

necessitam do sistema nos laboratórios da UTFPR e dos usuários rotineiros do

equipamento;

2. Codificar: iniciar a arquitetura do sistema. O diagrama elétrico e a

preparação dos códigos são planejados nessa etapa;

3. Construir: consiste na montagem do protótipo físico e implementação

do código para o microcontrolador ou sistema;

4. Testar: teste do protótipo que abrange hardware, firmware e software. A

etapa é necessária para entender o funcionamento do sistema e se há necessidade

de alterações;

5. Lançar: o sistema é disponibilizado para os usuários para testes mais

detalhados. Logo, a coleta do feedback do usuário do sistema é essencial;

6. Implementar: O sistema é colocado em produção de acordo com o

feedback do cliente. Apesar do lançamento para o usuário final, o sistema ainda

continua em observação para melhorias;

7. Operar: o desenvolvedor constantemente coleta feedback dos usuários

para melhoria do sistema;

8. Monitorar: a fase "final" do ciclo de DevOps é monitorar o ambiente

através da análise do comportamento do sistema, desempenho, erros e outros.

3.2 Controle de versão de código

Para auxiliar a metodologia DevOps, o projeto foi armazenado e gerenciado

através das ferramentas Git e Github (Figura 26), os quais permitem o controle de

versão dos códigos e gerenciamento de arquivos. Esses arquivos podem ser

acessados | através | do | link: | https://github.com/LincolnG4/Flowand-Pressure-

Controller.

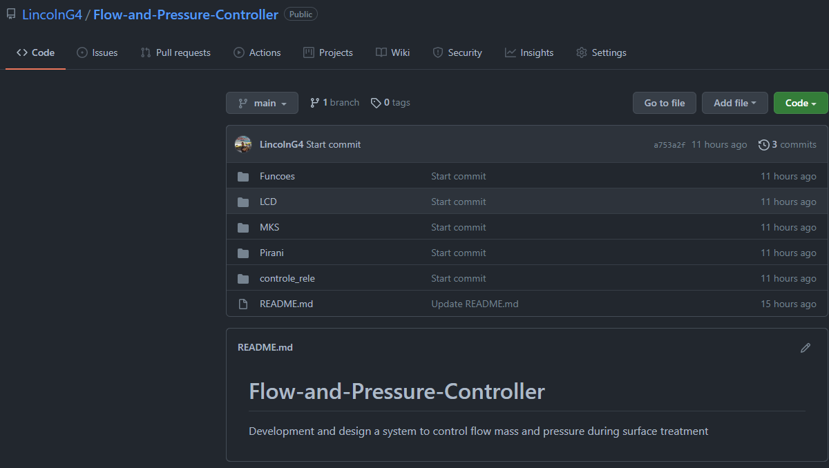
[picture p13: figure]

Figura 26 Controle de versão Github

O controle de versão é a prática de rastrear e gerenciar as alterações ao

códigofonte ao longo do tempo (Figura 27). A ferramenta para controle de versão

mantém registrado todas as modificações no código através de um banco de dados.

Caso ocorra um erro, o desenvolvedor pode retornar a versão anterior (GIT, 2021).

Além disso, o versionamento e armazenamento é disponibilizado em rede, auxiliando

na distribuição de atualizações e correções de erros para os usuários do produto

(MUDHOLKAR, 2017).

Figura 27 Esquema de versionamento de código

Além disso, o Github permite a realização de fork. O fork é uma cópia do

repositório na qual outros desenvolvedores podem realizar mudanças sem precisar

utilizar o repositório principal. Essas alterações podem ser propostas ao autor original

para integrar o novo código ao projeto.

3.3 Planejamento

Nesta etapa, os requisitos do projeto foram alinhados com os professores e

alunos que utilizam o reator do laboratório de tratamentos térmicos da UTFPR. Foram

realizadas reuniões mensais com 4 usuários dos reatores, a fim de coletar feedbacks

constantes e realizar testes no sistema.

Além disso, foi realizado uma visita acompanhada dos professores ao

laboratório da UTFPR, a fim de entender todo o sistema de funcionamento para o

equipamento. O sistema é inicialmente bombeado através de uma bomba de vácuo

mecânica. O conjunto, de 4 MFC (GE50A 500 SCCM MKS Instrument), é responsável

por gerenciar a passagem de cada gás que define a mistura gasosa dentro da câmara

(Figura 28).

Figura 28 – Esquemático simplificado do sistema de tratamento de superfície

Além do desenho esquemático do sistema, foi realizado uma entrevista com

os professores para entender algum dos requisitos para controlar o sistema. Logo, foi

levantado, requisitos funcionais:

- Ler e controlar o fluxo de massa através de sensores MFC durante um

período estipulado pelo usuário;

- Ler a pressão no reator através de um sensor Pirani;
- Gerar relatório com todas as medições realizadas;
- Calcular e corrigir as leituras de acordo com os gases utilizados;
- Alertar e prevenir erros de medição.

Os requisitos não funcionais:

- Ler e controlar o fluxo de massa através do sensor MFC GE50A 500

SCCM MKS Instrument;

- Entrada para 4 MFC’s;
- Ler a pressão através do sensor Pirani APGX-M-NW16/ALI Edwards;
- Exibir a pressão em Torr
- O relatório deve ser gerado ao fim de cada medição.
- O relatório deve identificar sensor, data e hora de cada valor;

Portanto, o sistema final centraliza as atividades de medir a pressão através

do módulo Pirani e controlar os 4 módulos de controle de fluxo de massa (Figura 29).

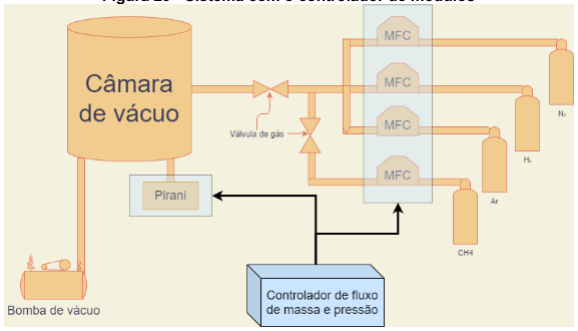
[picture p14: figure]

Figura 29 Sistema com o controlador de módulos

4 DESENVOLVIMENTO DO PROTÓTIPO

O desenvolvimento deste projeto foi dividido em 3 grandes grupos: hardware,

firmware e software. O hardware desenvolvido consiste em uma placa de circuito

impresso que suporta um microcontrolador e circuitos que auxiliam a entrada e saída

dos sinais elétricos. O firmware consiste nas rotinas programadas no microcontrolador

que analisam os sinais de entrada e, a partir deles, geram os sinais de saída. O

software, consiste em uma API desenvolvida em JavaScript na plataforma Apps Script

do Google Sheets e o Grafana para criação de dashboards.

Para o hardware, a PCB e os circuitos apresentados foram desenhados e

simulados no KiCad 6.0 e Schematic Editor. O desenho CAD do case foi modelado no

FreeCAD 0.19 e preparação para impressão 3D no software Cura 3D.

O firmware foi escrito em C++ utilizando o Visual Studio Code como editor. E

o firmware da tela touch screen foi desenvolvido no software do fabricante: Nextion

Editor. A interface gráfica do display foi desenhada utilizando o software Photopea.

Todas a ferramentas utilizadas são gratuitas e de código aberto.

4.1 Hardware

O desenvolvimento do hardware foi dividido em 3 categorias: “função leitura

de pressão”, “função de controle de fluxo de massa” e “registro de dados e

visualização”. Sendo a primeira responsável pelo tratamento do sinal do Pirani; a

segunda responsável pelo tratamento do sinal do MFC; e a última responsável por

coleta, upload e visualização dos dados gerados. Esta divisão foi esquematizada na

Figura 30.

Figura 30 Esquemático Hardware

4.1.1 Microcontrolador

Neste trabalho, os microcontroladores Arduino Mega e ESP32 foram

avaliados como possíveis soluções que atendem as necessidades do projeto. Assim,

foi elaborado o Quadro 2 que visa comparar as especificações técnicas dos dois

microcontroladores.

Quadro 2– Comparação Arduino Mega x ESP32

Em geral, o ESP32 possui especificações técnicas melhores de hardware do

que o Arduino Mega. Além disso, por ele ser dualcore, há a possibilidade de

MultiThreading, ou seja, paralelizar atividades em seu software, como por exemplo a

realizar medições simultâneas dos sensores. Porém, de acordo com o manual técnico

do produto (ESPRESSIF 2019) e testes realizados por outros usuários Figura 31 e 32,

os resultados de medições acima de 3 V (tensão em aprox. 2.450 mV), a exatidão do

ADC piora drasticamente (Figura 32). Por padrão, há ± 6% de diferença nos resultados

medidos entre os chips. Além disso, esse microcontrolador tem sinal de saída e

entrada equivalente a 3 V. A redução dos sinais de entrada e a amplificação dos sinais

de saída podem prejudicar a exatidão deles.

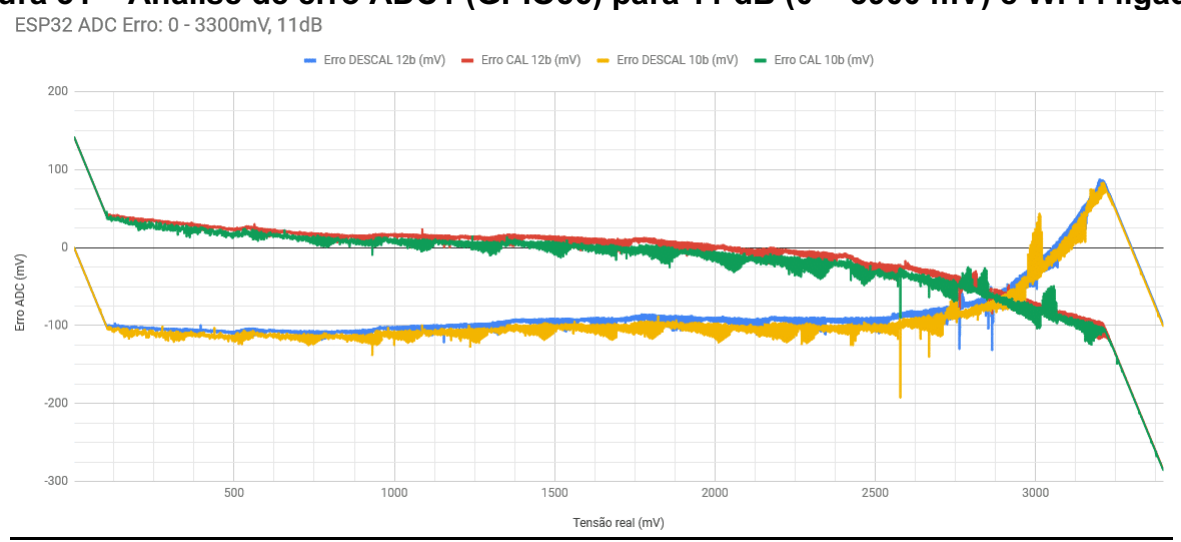
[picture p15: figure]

Figura 31 – Análise de erro ADC1 (GPIO36) para 11 dB (0 – 3900 mV) e Wi-Fi ligado

Fonte: Morais (2019) Arduino MEGA 2560 | ESP32
Alimentação | 5V | 3,3V
Entrada Regulada (VIN) | 7 ~ 12V | 5 ~ 9V
Corrente de Consumo: | Media de 70mA | Media de 80mA
Processador: | ATmega2560 RISC com até 16 MIPS | Xtensa® Dual-Core 32-bit LX6
Frequência de Operação: | 0 ~ 16MHz | 80MHz ~ 240MHz
Memoria FLASH: | 256 KB | 4MB
Memoria RAM/SRAM: | 8 KB | 520KB
Memória ROM/EEPROM | 4 KB | 448KB
Pinos de I/O: | 54 pinos | 34 pinos
Conversores ADC (Analógico para Digital): | 16 ADC com 10-bit de resolução (1024 bits) | 18 ADC com 12-bit de resolução (4096 bits)
Conversores DAC (Digital para Analógico): | - | 2 DAC com 8-bit de resolução (256 bits)
WiFi: | - | 2,4 GHz, 802.11 b/g/n/e/i (802.11n até 150 Mbps)
Bluetooth: | - | Bluetooth Low Energy v4.2 (BLE)
Temporizadores | 4 Timers, 2 de 16-bit e 2 de 16bit | 4 Timers de 64-bit
Interfaces de Módulos | I2C, SPI, 4 UART e LED PWM | SPI, SDIO, LED PWM, Motor PWM, I2S e IR

Figura 32 – Leitura osciloscópio x Leitura ESP32

Fonte: Koyanagi (2018)

Assim, para usufruir de toda a capacidade do hardware ESP32 e das suas

portas analógicas, seria necessário um longo período de testes e ajustes a fim de

garantir o perfeito funcionamento. Somado a isso, este trabalho foi realizado durante

as restrições da pandemia, que resultaram na redução do tempo do período letivo e

em dificuldades para utilização do laboratório da universidade.

Logo, a fim de cumprir os objetivos deste trabalho dentro do período

estabelecido, o Arduino Mega foi selecionado como microcontrolador. O Arduino Mega

atende todos os requisitos de programação e não necessita de calibração das suas

portas ADC. Junto a ele, será usado um ESP01 para gerar conexão Wi-Fi.

4.1.2 Circuito de leitura de pressão

O sensor Pirani Edwards APGX-M-NW16/ALI foi utilizado na leitura da

pressão do reator. O sinal de saída do sensor varia entre 0 e 10 V e é submetido a um

divisor de tensão, formado por dois resistores de 4.7 kΩ, e um filtro passabaixas, um

resistor de 220Ω e capacitor de 1µF (Figura 33). Com isso, o sinal é reduzido pela metade para atender a tensão máxima de 5 V do Arduino Mega. A pinagem do sensor

foi representada no Quadro 3, conforme o manual Edwards (2015). A numeração da

pinagem do conector Pirani na Figura 33 se difere ao Quadro 3 devido ao software

inverter os pinos por conta do modelo RJ45 escolhido

Figura 33 Circuito leitura Pirani

Quadro 3 – Pinagem RJ45 Pirani Edwards
Sinal | Pino RJ45
+15 à +36 V Alimentação | 1
GND | 2
Sinal de saída de medição pressão (0-10 V) | 3
| 4
GND | 5
| 6
| 7
| 8

4.1.2.1Compatibilidade

O circuito foi projetado para atender sensores Pirani com alimentação mínima

de 24 V e sinal de saída de 10 V. Assim, no Quadro 4, foram listados alguns dos

sensores compatíveis com o hardware.

Quadro 4 – Sensores Pirani compatíveis

4.1.3 Circuito de leitura e controle do fluxo de massa

Foram utilizados 4 sensores MFC GE50A 500 SCCM da MKS Instruments

para leitura e controle do fluxo de massa. A pinagem foi representada no Quadro 5

segundo o manual do fabricante MKS (2013).

Quadro 5 Pinagem MFC DB9
Sinal | Pino DB9
Abertura/Fechamento válvula | 1
Sinal de saída (0 5 V) | 2
+15 à +25 VDC Alimentação | 3
GND | 4
Sem conexão | 5
Set point Input, 0-5 V | 6
GND | 7
GND | 8
Teste ponto de válvula | 9

O controle da válvula (Set point) é submetido a um filtro pi – um resistor

de 470Ω e um capacitor de 1µF cada . Um transistor BC337 foi utilizado como chave,

no pino 1, para garantir o fechamento completo da válvula (Figura 34).

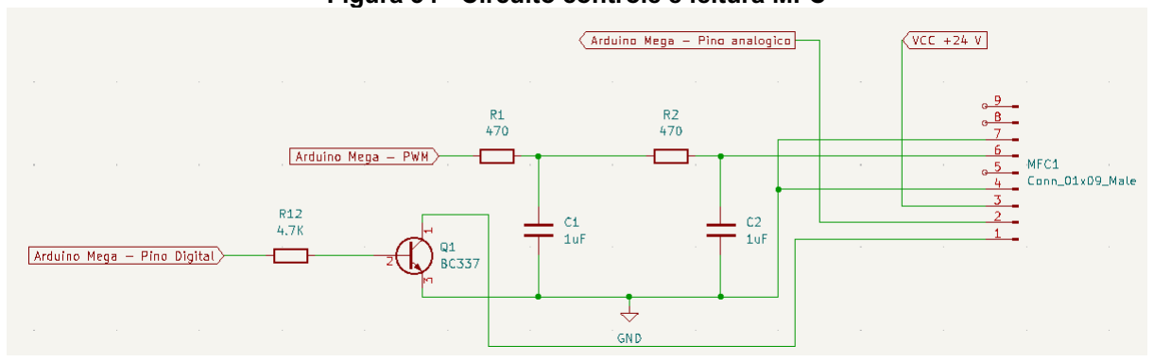
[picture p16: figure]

Figura 34 Circuito controle e leitura MFC

Sensor Pirani Compativeis | Necessidade de cabo RJ45 compatível
Edwards APGX-M-NW16/ALI | Não
Edwards APG100 | Não
Edwards APG200 | Não
BPG402-Sx ATM to Ultra-High Vacuum Gauge | Sim
MKS EtherCAT® 901P-17020 Micro Pirani-Piezo Loadlock Vacuum | Sim
PTR 90 N PENNINGVAC 230070V02 | Não
CX-PRN10 Smart Pirani Vacuum Gauge | Não

4.1.3.1Compatibilidade

O circuito foi projetado para atender controladores de fluxo de massa com

alimentação mínima de 24 V, sinal de entrada de 5 V e sinal de saída de 5 V. No

Quadro 6 foram listados controladores de fluxo de massa compatíveis.

Quadro 6 – Compatibilidade de MFC

4.1.4 Registro de dados e visualização

4.1.4.1Tela sensível ao toque

A tela utilizada é a Nextion serial touch 320x240 pixels (Figura 35). Esse

display possui um processador próprio, permitindo a renderização de imagens e

funções. Assim, o Arduino prioriza as tarefas principais: leitura e processamento de

sinais. A tela é composta de quatro pinos: dois pinos são para alimentação 5V e terra;

dois pinos para comunicação serial (Tx e Rx).

Os pinos seriais Rx e Tx foram conectados, respectivamente, aos pinos 18

(Tx) e 19 (Rx) do Arduino Mega, equivalente ao Serial1 do microcontrolador.

Figura 35 – Display Nextion 320x240 pixels

Fonte: Nextion (2022)

Sensor MFC Compativeis | Necessidade de cabo DB9 compatível
G-Series GM50 MKS | Não
MFC GF100 Brooks Instrument | Não
GC1 Series Air Mass Flow Controller Dakota Instruments | Sim
Whisper™ MCW–Series- Alicat | Sim
SLA5800 Brooks Instrument | Sim
EL-FLOW® Select Bronkhorst | Sim
MFC SLA5800 Brooks Instrument | Não

Outros displays de toque foram estudados, como o WinWin tft 2.4 que é

compatível com as bibliotecas gráficas LVGL de código aberto, mas a falta de um

editor de GUI e a pouca quantidade de tutoriais disponíveis foram decisivos para a

escolha do Nextion como display.

4.1.4.2 Módulo leitura e escrita em cartão microSD

O módulo de leitura e escrita em cartão microSD, Figura 36, foi utilizado para

armazenar as medições do sensor Pirani e dos controladores de fluxo de massa. Esse

módulo tem capacidade de leitura de dois tipos de cartão de memória: o cartão Micro

SD tradicional e o Micro SDHC cartão de memória de alta velocidade.

Figura 36 – Módulo leitura e escrita em cartão microSD

Fonte: Last Minute Engineers (2022)

Esse módulo necessita de uma comunicação SPI (Serial Peripheral Interface),

a qual se aplica aos pinos do Arduino Mega: 50 (MISO), 51 (MOSI), 52 (SCK), 53 (CS)

4.1.4.3 Realtime clock (RTC)

O módulo RTC ds1302 (Figura 37) foi utilizado para uma maior exatidão do

controle do tempo. O módulo temporiza e registra a data e hora da coleta dos dados

dos sensores que são salvos no cartão microSD.

Figura 37 Módulo RTC ds1302

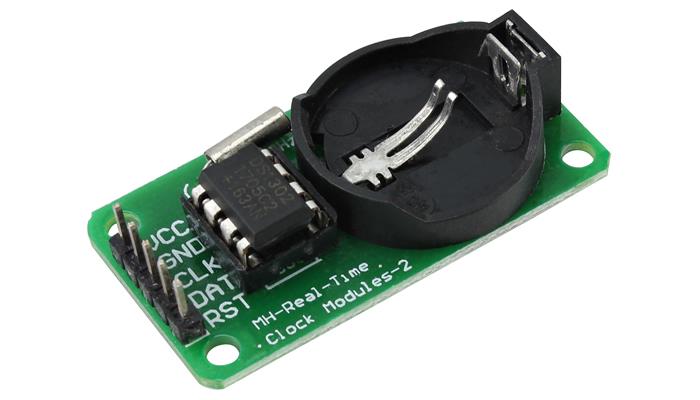
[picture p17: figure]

Fonte: Usina Info (2022)

O RTC necessita de uma bateria CR2032 para manter a contagem exata do

tempo gravado em sua memória, mesmo quando o Arduino é desligado. A bateria tem

um tempo estimado de 10 anos de vida útil.

O pino CLK é conectado ao pino 8 do Arduino e os pinos DAT e RST estão,

respectivamente, conectados aos pinos 22 e 23.

4.1.4.4 ESP01 (ESP8266 Wi-Fi)

O microcontrolador ESP01 foi utilizado como módulo de conexão Wi-Fi para

o Arduino Mega. O módulo contém 8 pinos: VCC (3.3V), GND, Rx, Tx, GPIO0, GPIO2,

RST e CH_PD. Para esse projeto, foram utilizados os pinos de alimentação e o pino

Rx para comunição serial com o Arduino Mega através da porta 16 (Tx), equivalente

ao Serial2 do Mega.

Através da porta serial, o Arduino envia as mensagens referente as medições

dos sensores para o módulo Wi-Fi, que envia as mensagens para o Google Sheets.

A função de envio para a rede será explicada com detalhes dentro do tópico de

Firmware e Software.

4.1.4.5 Fonte de alimentação

A alimentação dos principais componentes da placa se dá com uma tensão

de 24V. Assim, foi selecionado a fonte Knup (Figura 38) de 24 Volts e 4A.

Figura 38 Fonte Knup 24V

Fonte: Azob (2022)

O módulo regulador de tensão LM2596 (Figura 39) foi utilizado para reduzir

a tensão até 7 V para alimentar o Arduino Mega com a tensão recomendada em seu

datasheet (ARDUINO, 2022). O módulo trabalha como um conversor DC-DC no modo

Step Down. A tensão de saída pode ser ajustada entre 1.5 e 35 V, tendo como entrada

3.2 a 40 V.

Figura 39 Módulo regulador de tensão LM2596

Fonte: Texas Instruments (2022)

4.1.4.6 Placa de circuito impresso

A placa de circuito impresso foi desenvolvida em formato de shield, que está

conectada a uma placa base. O circuito eletrônico e a PCB foram projetadas no

software KiCad 6.0 (Figura 40).

Figura 40 – Esquema eletrônico

A placa é formada por 2 camadas e dimensão 147,3 mm x 68,6 mm x 1,6 mm

(Figura 41 e 42). As rotas da PCB foram calculadas no software Schematic Editor. Por

fim, os arquivos gerber foram gerados para a fabricante JLCPCB (jlcpcb.com). Os

arquivos gerber armazenam, em formato vetorial ASCII, os detalhes do projeto para

configuração das máquinas camadas de cobre, dados de perfuração, máscara de

solda, legenda e outros. A placa custou 20 reais/unidade (produto + frete).

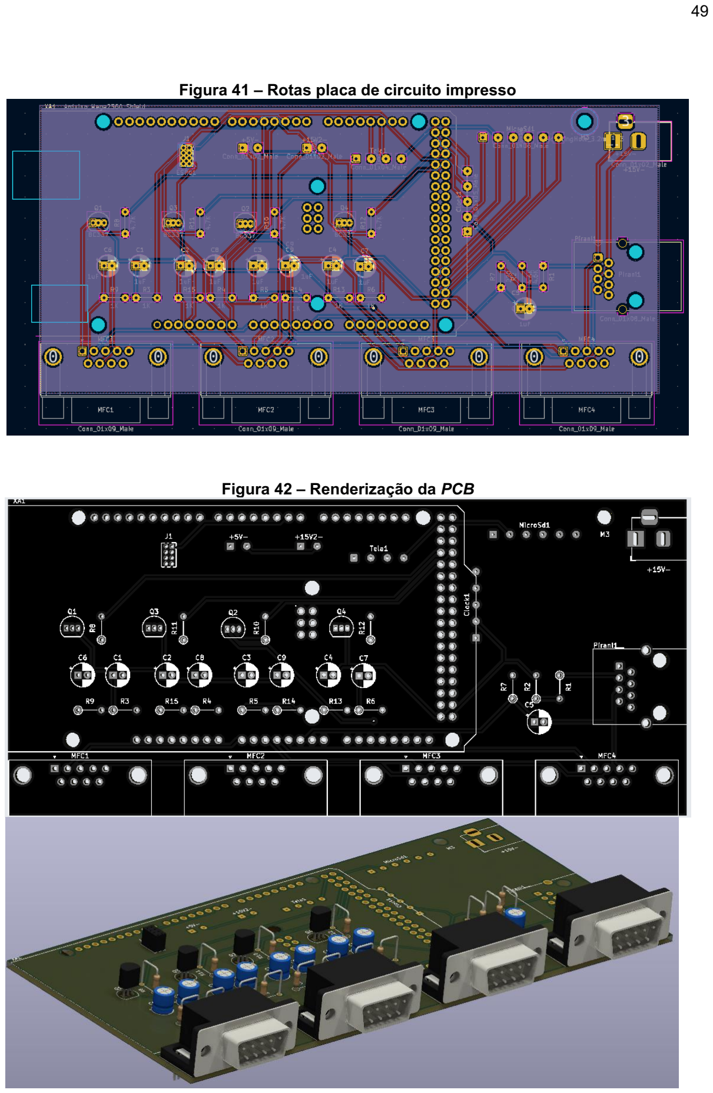
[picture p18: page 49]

Figura 41 – Rotas placa de circuito impresso

Figura 42 – Renderização da PCB

4.1.4.7 Case do produto e montagem

O case do protótipo é formado por um gabinete e uma tampa (Figura 43).

Figura 43 – Montagem gabinete e tampa

As medidas do gabinete são 165,5 x 74,6 x 25 mm (Figura 44). Ele contém

frestas para ajudar no resfriamento do hardware já que o mesmo não possui nenhum

sistema de refrigeração, como coolers ou ventoinhas. A montagem da PCB shield com

o Arduino é através de encaixe e não necessita de parafusos. Além disso, existe um

relevo junto a aba lateral direita para apoio da PCB. A tampa é parafusada ao gabinete

através dos 4 suportes externos.

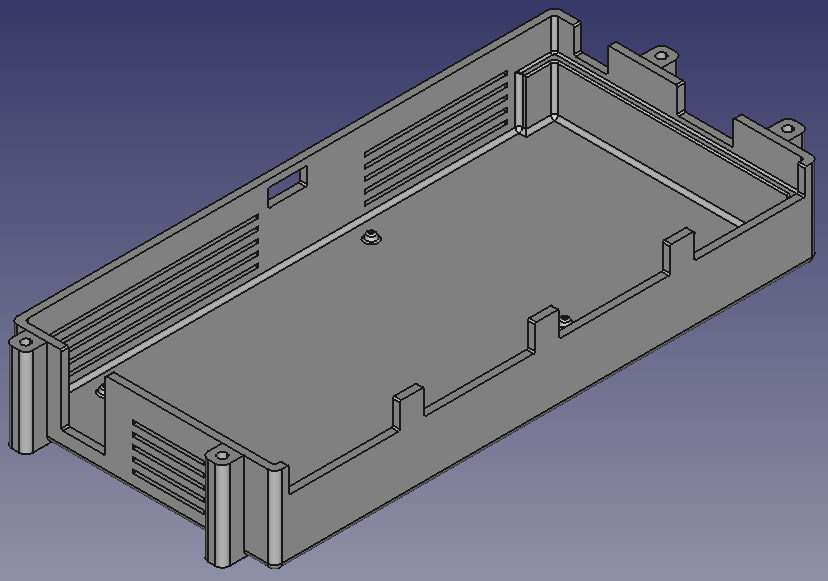
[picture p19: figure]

Figura 44 – Gabinete CAD

As medidas da tampa são 165.5 x 74.6 x 16 mm (Figura 45). Além disso,

possui entrada para parafusar a tela touch (M3x8mm) e os apoios externos para

parafusar com o gabinete (M3x10mm).

Figure 45 – Tampa CAD

O case do protótipo foi impresso 3D a partir de PLA. O PLA foi selecionado

por conta do seu baixo custo, facilidade de impressão e parametrização. O software

Cura 3D foi utilizado para a configuração da impressão (Figura 46). Foram utilizados

os parâmetros: 0.2 mm de altura/camada e preenchimento de 10% (Figura 47).

Figura 46 – Posicionamento e configuração Cura 3D

Figura 47 Parâmetros de impressão

Assim, o resultado da montagem é apresentado na Figura 48. A parte frontal

do projeto contém as entradas para os controladores de fluxo de massa e a lateral

direita contém as entradas de leitura do sensor Pirani e alimentação do sistema.

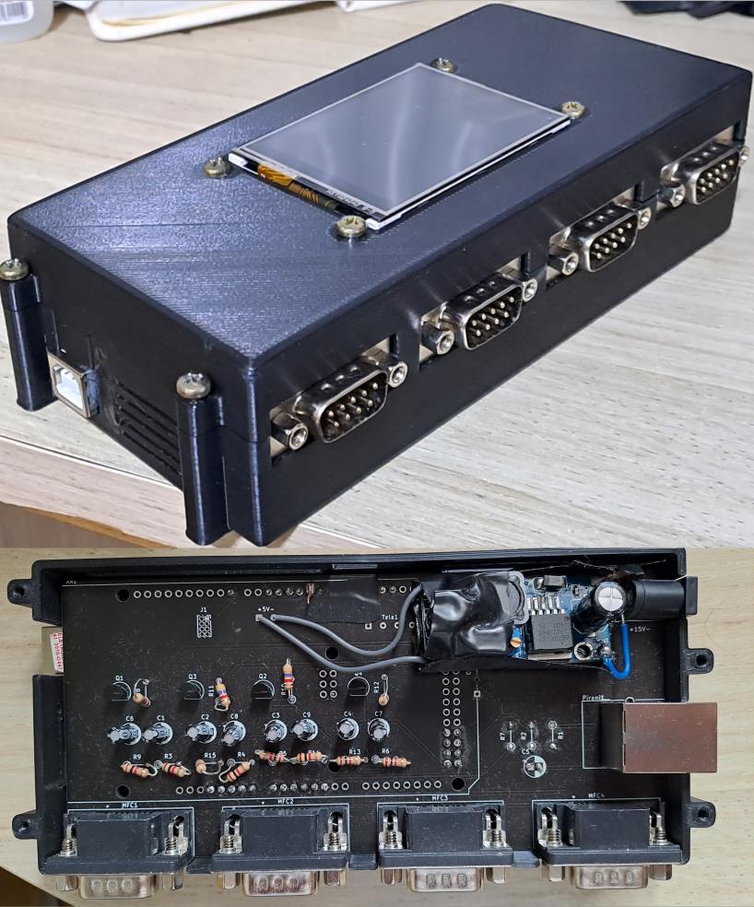
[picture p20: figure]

Figura 48 – Montagem do protótipo

4.2 Firmware

O firmware é dividido em três partes: tela Nextion, Arduino Mega e ESP01. O

primeiro faz o controle da interface gráfica, o segundo faz a rotina de leitura dos

sensores e o último o envio das medições para a internet. O diagrama de sequência

é representado na Figura 40 e o diagrama de funcionamento é representado no

esquemático da Figura 50.

Figura 49 – Diagrama de sequência

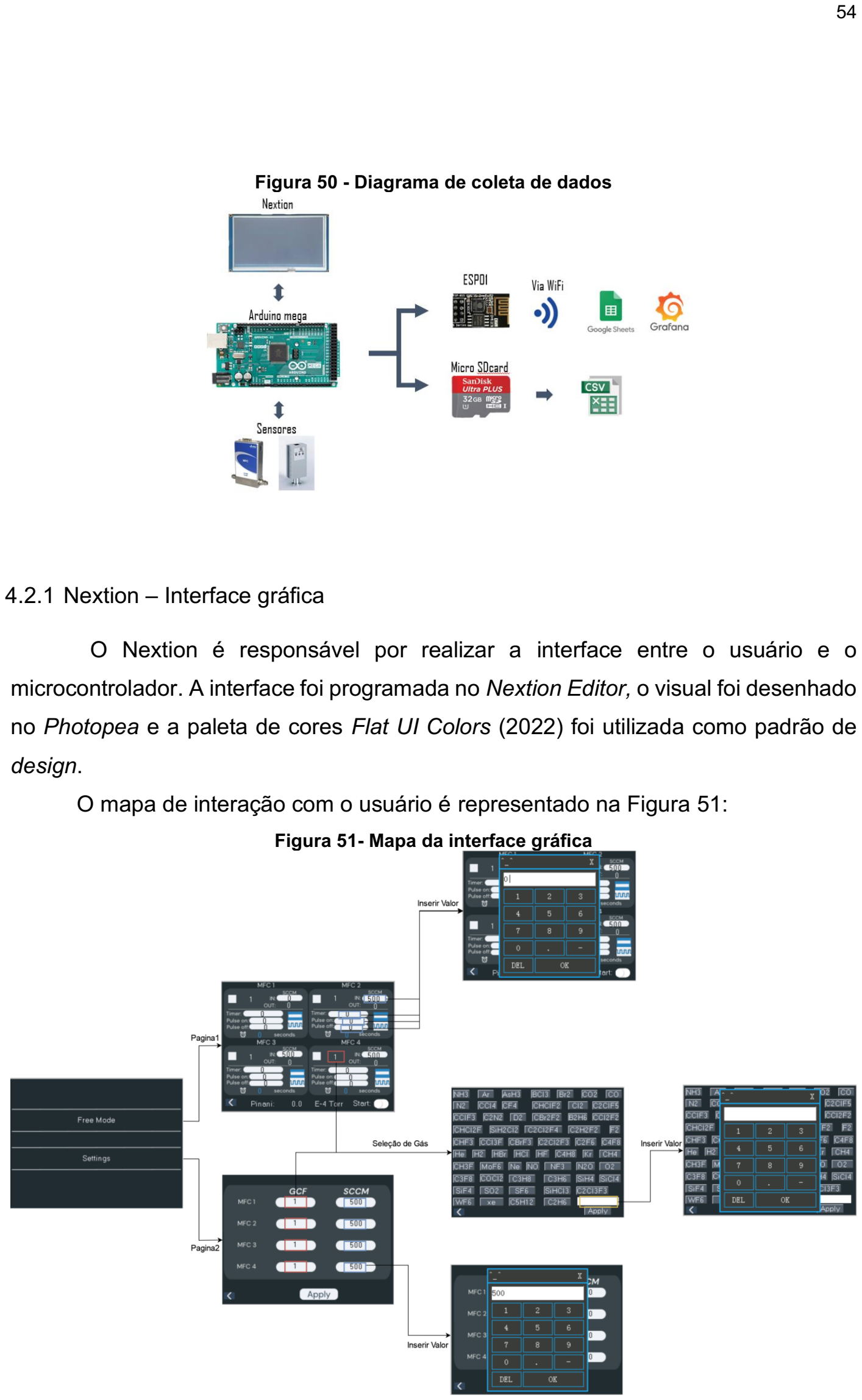
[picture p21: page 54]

Figura 50 Diagrama de coleta de dados

4.2.1 Nextion – Interface gráfica

O Nextion é responsável por realizar a interface entre o usuário e o

microcontrolador. A interface foi programada no Nextion Editor, o visual foi desenhado

no Photopea e a paleta de cores Flat UI Colors (2022) foi utilizada como padrão de

design.

O mapa de interação com o usuário é representado na Figura 51:

Figura 51- Mapa da interface gráfica

No menu de “Settings”, é possível configurar o fator de correção do gás

calibrado e inserir o SCCM máximo para cada equipamento (Figura 52). Os valores

dos fatores de correção dos gases cadastrados no hardware são selecionados

(Apêndice B) com base na tabela da MKS (2022). Além disso, há a possiblidade do

usuário inserir um fator manualmente (Figura 53).

Figura 52 – Menu de configurações “Settings”

Figura 53 – Menu de gases cadastrados

A leitura dos sensores e controle dos MFC’s são realizados no menu “Free

Mode” (Figura 54). Os controladores de fluxo de massa funcionam independentes um

do outro, ou seja, cada configuração de tempo, função, abertura de válvula e gás são

específicas para cada um. Além disso, através das caixas de seleção, é possível

selecionar quais os controladores que irão rodar durante a medição.

As funções programadas são: Continuo e pulsado. No modo contínuo, o

microcontrolador roda uma rotina de abertura constante da válvula até o fim do

cronômetro inserido no Timer (segundos). O modo pulsado, o microcontrolador roda

uma rotina de abertura e fechamento da válvula até o fim do cronômetro inserido no

campo Timer. Os tempos dessa abertura e fechamento são inseridos nos campos

“Pulse On” e “Pulse Off”.

A medição é iniciada assim que a “Chave Mestre” for ligada. Enquanto essa

chave está aberta, não é possível sair do menu “Free Mode”.

Figura 54 – Menu de controle dos sensores “Free Mode”

4.2.2 Arduino Mega

O Arduino Mega é responsável por armazenar as configurações dos sensores,

receber os inputs do usuário através da tela Nextion, controlar e ler os sensores. Os

códigos em C++ foram organizados em 3 partes: o código principal (“main.ino”), as

bibliotecas de função (pasta “lib”), Figura 55, e os arquivos de configurações dos equipamentos (pasta “config”). As principais funções e bibliotecas serão explicadas

de forma geral durante este trabalho (Apêndice D).

Figura 55 Estrutura dos arquivos

4.2.2.1Biblioteca sensor MFC

A biblioteca do sensor MFC contém 3 funções: “MFCPwmON”,

“MFCPwmClose” e “MFCRead”. A primeira função recebe o input de abertura da

válvula do MFC, converte em um sinal PWM para abertura da válvula considerando

o valor de SCCM máximo configurado pelo usuário e atualiza o valor na tela (Código

1).

Código 1 Função "MFCPwnON"

/*

* Send PWM signal to open valve

* @param PinPWM timer timerText SCCMValveOpen CalibratedSCCM
*/

void MfcPwmON(int PWM_INPUT,int delta,NexText t,NexNumber n,uint32_t

mfcSCCM){

char buffer[100] = {0};

uint32_t val;

n.getValue(&val); //Request object from Nextion

val = map(val, 0, mfcSCCM, 0, 255);

analogWrite(PWM_INPUT, val);

itoa(delta,buffer, 10);
t.setText(buffer); //Send value to object Nextion

}

A função “MFCPwmClose” envia sinal para acionar o transistor, fechando a

válvula, e o sinal PWM é colocado em nível lógico baixo (Código 2).

Código 2 Função "MFCPwmClose"

/*

* This sends PWM zero to close valve

* @param t_calibrate MFC SCCM value

* @return new float MFC SCCM calibration
*/

void MfcPwmClose(int PWM_INPUT,int delta,NexText t,int Close_MFC){

char bufferclose[100] = {0};

digitalWrite(Close_MFC, HIGH);

analogWrite(PWM_INPUT, 0);

itoa(delta,bufferclose, 10);

t.setText(bufferclose);

}

A última função, “MFCRead”, lê o retorno de abertura de válvula do

controlador de fluxo de massa e corrige a saída SCCM de acordo com o fator de

correção do gás e da calibração do equipamento utilizado (Código 3).

Código 3 Função "MFCRead"

/*

* This read MFC and applies gas correction factor

* @param MFC_number T_print textMFCOut GasFactor mfcSCCM

* @return MeasureMFC
*/

float MFCRead(int MFC,NexText t,NexText t_out, float

Calibrated_MFC,uint32_t mfcSCCM){

char mfcOutputString[10];

float gas_factor_in;

float output_MFC_factor;

char bufferText[10];

MFC_V =
(mfcSCCM*(sinalMKS/SinalMCU)*((SinalMCU*(analogRead(MFC)))/bitsMCU))/SinalM

CU;

memset(bufferText, 10, sizeof(bufferText));

t_out.getText(bufferText, sizeof(bufferText));

gas_factor_in = atof(bufferText);
output_MFC_factor = float(MFC_V)*(gas_factor_in/Calibrated_MFC);

dtostrf(output_MFC_factor, 1, 2, mfcOutputString);

t.setText(mfcOutputString);

return output_MFC_factor;

}

4.2.2.2Biblioteca sensor Pirani

A | biblioteca | do | sensor | Pirani | contém | 2 | funções: | “PiraniRead”,

“piraniUpdateScreen”. A primeira função lê a medição do sensor e converte de Volts

para Torr. Porém, caso haja controladores de fluxo de massa rodando em paralelo, a

função corrige a medição aplicando o fator de correção dos gases, considerando a

porcentagem de fluxo de entrada para cada controlador (Código 4).

Código 4 Função "PiraniRead"

/*

* Read Pirani

* This get signal from Pirani, converts from V to Torr and applies a

correction factor considering the gas %.

* If no MFC is turned ON, it won't apply a correction factor

* @params Checkbox1_4, GasFactor1_4, MFC_valve

* @return Pirani in torr
*/

float PiraniRead(uint32_t checkbox1,uint32_t checkbox2,uint32_t

checkbox3,uint32_t checkbox4,NexText t_gas1,NexText t_gas2,NexText

t_gas3,NexText t_gas4,int mcfOutput1,int mcfOutput2,int mcfOutput3,int

mcfOutput4){
float Pirani_V = 0;

float totalFlow=0;

float correctionFactor=1;

char bufferText[10];

char bufferText2[10];

char bufferText3[10];

char bufferText4[10];

float gas_factor_1 = 1;

float gas_factor_2 = 1;

float gas_factor_3 = 1;

float gas_factor_4 = 1;

Pirani_V =
(sinalPirani/SinalMCU)*((SinalMCU*(analogRead(Read_Pirani)))/bitsMCU);

if(checkbox1==0 && checkbox2==0 && checkbox3==0 && checkbox4==0){ //if

mfc's are turned off

Pirani_Torr = 10000.00*(pow(10,(Pirani_V-6.125)));

return Pirani_Torr;

}

else{ //mfc's are turned off, calculate % gas and apply correction factor

to Pirani measure

if(checkbox1==1){

totalFlow = totalFlow + mcfOutput1;

memset(bufferText, 10, sizeof(bufferText));

t8.getText(bufferText, sizeof(bufferText));

gas_factor_1 = atof(bufferText);

}

if(checkbox2==1){

totalFlow = totalFlow + mcfOutput2;

memset(bufferText2, 10, sizeof(bufferText2));

t19.getText(bufferText2, sizeof(bufferText2));

gas_factor_2 = atof(bufferText2);

}

if(checkbox3==1){

totalFlow = totalFlow + mcfOutput3;

memset(bufferText3, 10, sizeof(bufferText3));

t20.getText(bufferText3, sizeof(bufferText3));

gas_factor_3 = atof(bufferText3);

}

if(checkbox4==1){

totalFlow = totalFlow + mcfOutput4;

memset(bufferText4, 10, sizeof(bufferText4));

t21.getText(bufferText4, sizeof(bufferText4));

gas_factor_4 = atof(bufferText4);

}

correctionFactor = checkbox1*(mcfOutput1/totalFlow)*gas_factor_1 +

checkbox2*(mcfOutput2/totalFlow)*gas_factor_2 +

checkbox3*(mcfOutput3/totalFlow)*gas_factor_3 +

checkbox4*(mcfOutput4/totalFlow)*gas_factor_4;

Pirani_Torr = 10000.00*(pow(10,((Pirani_V*correctionFactor)-6.125))); // convert V to Torr and applies correction Factor

return Pirani_Torr;

}

}

A última função atualiza a tela Nextion com o valor de Pirani calculado na

função anterior (Código 5). Porém, conforme o manual do fabricante Edwards (2007),

as medições abaixo de 2 V e acima de 9 V são faixas de erro -Figura 56-. Os erros

mapeados são apresentados no Quadro 7. Assim, a função alerta o usuário do erro

colorindo de vermelho o valor de medição na tela.

Código 5 Função "piraniUpdateScreen"

void piraniUpdateScreen(float Pirani_V){

dtostrf(Pirani_V, 4, 2, buff);
t10.setText(buff); // Print on screen the Pirani value

if(Pirani_V<0.7498 || Pirani_V>7498942.0933){ t10.Set_font_color_pco(57959); //Set Object to change color white

}

else{
t10.Set_font_color_pco(61342); //Set Object to change color

}

}

Figura 56 Transformação de tensão para pressão

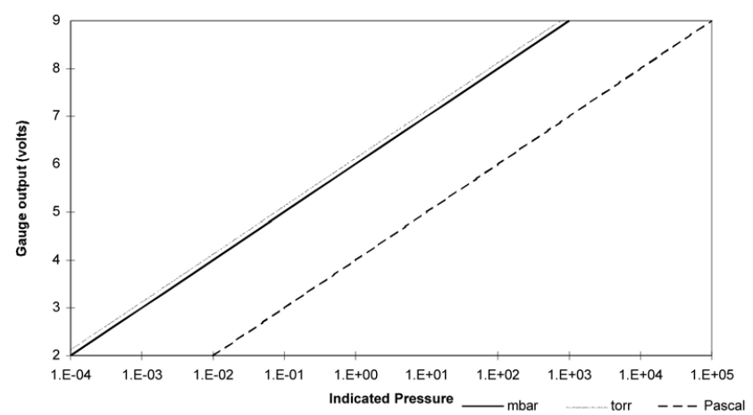
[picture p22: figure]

Fonte: Edwards (2007)

Quadro 7 Mapeamento de erros
Indicação de erro | Sinal de saída
Filamento quebrado | 9,5 V
Erro de calibração | 9,6 V

4.2.2.3Modo de operação

Os controladores de fluxo de massa têm 2 modos de operação: contínuo e

pulsado. O modo de operação contínuo mantém a válvula aberta com valor constante até o fim do cronômetro configurado pelo usuário (Código 6). Além disso, durante a

operação, as medições são salvas no arquivo “CSV”.

Código 6 Modo contínuo

/*

* MFC - Linear

* This 'If' starts the Linear function that controls the valve with

constant value for a period of time.

* During the ON period, it saves all measure into a CSV file in microSDcard */

if(MFC1_mode_linear==1 && MFC1_mode_pulse==0){
MFC_CSV_1 = SD.open("MFC1.csv", FILE_WRITE); //Create a CSV file

if(timer_enable == 0){ //first time run

n1.getValue(&timerMFC1); // Get time to be Opening&Running

start_mfc1 = unix; // Get time start reference

timer_enable = 1;

}

delta = unix - start_mfc1;

if(timerMFC1 >= delta){
digitalWrite(Close_MFC1, LOW); // Open valve

MfcPwmON(PWM_INPUT1,delta,t15,n0,mfcSCCM1);

MFC1_value = MFCRead(MFC,t11,t8,Calibrated_MFC_1,mfcSCCM1);

String message1 = TimeString + "," + String(MFC1_value);

WriteSD(MFC_CSV_1,message1);

}

else{

MfcPwmClose(PWM_INPUT1,delta_pulse,t15,Close_MFC1); c0.setValue(0); //uncheck checkbox object Nextion

checkbox1 = 0;

timer_enable = 0;

int delta = 0;

}

}

O modo de operação pulsado (Código 7) varia entre a válvula aberta e fechada

até o fim do cronômetro. Ou seja, a medição se encerra ao fim do cronometro

independentemente do estado da válvula. O cálculo dessa variação de estado é

explicado na Figura 57.

Figura 57 Esquema de abertura e fechamento

Código 7 Modo pulsado

/*

* MFC - Pulse

* This 'If' starts the Pulse function that controls the valve switching

from ON and OFF.
* During the ON/OFF period, it saves all measure into a CSV file in micro

SDcard
*/

if(MFC1_mode_pulse==1 && MFC1_mode_linear==0){

//CREATE SAVE A SD CARD

MFC_CSV_1 = SD.open("MFC1.csv", FILE_WRITE);

if(timer_enable_pulse == 0){
n1.getValue(&timerMFC1_pulse); // Get total timer

n8.getValue(&timerMFC1_pulse_on); // Get timer to open pulse

n9.getValue(&timerMFC1_pulse_off); // Get timer to close pulse

total1 = timerMFC1_pulse_on + timerMFC1_pulse_off;
cycle_on = timerMFC1_pulse_on/float(total1);

start_mfc1_pulse = unix;

timer_enable_pulse = 1;
//Serial.println("[INFO] - MFC1 - Turned ON");

}

delta_pulse = unix - start_mfc1_pulse;

if(timerMFC1_pulse > delta_pulse){
if( ((delta_pulse%total1)/float(total1)) < cycle_on ){ // open pulse

digitalWrite(Close_MFC1, LOW); //OPEN VALVE

MfcPwmON(PWM_INPUT1,delta_pulse,t15,n0,mfcSCCM1);

MFC1_value = MFCRead(MFC,t11,t8,Calibrated_MFC_1,mfcSCCM1); String message1 = TimeString + "," + String(MFC1_value); //

WriteSD(MFC_CSV_1,message1);

}

else{ // close pulse

MfcPwmClose(PWM_INPUT1,delta_pulse,t15,Close_MFC1);

MFC1_value = MFCRead(MFC,t11,t8,Calibrated_MFC_1,mfcSCCM1);

String message1 = TimeString + "," + String(MFC1_value);

WriteSD(MFC_CSV_1,message1);

}

}

else {

MfcPwmClose(PWM_INPUT1,delta_pulse,t15,Close_MFC1); c0.setValue(0); //Send to object to close Nextion Checkbox

checkbox1 = 0;

delta_pulse= 0;

timer_enable_pulse = 0;

}

}

4.2.3 ESP01 – conexão Wi-Fi

O ESP01 é responsável por coletar as medições do Arduino Mega e enviar

para o Google Sheets através da API desenvolvida na plataforma App Script do

Google (Código 8). Além disso, esse microcontrolador é responsável por gerenciar a

conexão Wi-Fi. Ao ligar, caso a conexão Wi-Fi falhe, o ESP01 inicia um servidor web

para que o usuário troque a conexão e senha (Figura 58). Esse servidor tem IP fixo

(10.0.1.32) e o nome da conexão é "UTFPR_IOT_10.0.1.32" e a senha foi

disponibilizada para os usuários.

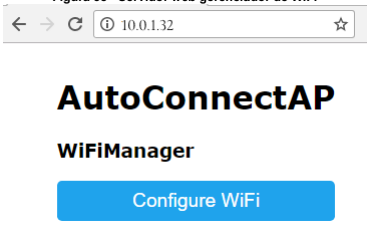
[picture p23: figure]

Figura 58 Servidor web gerenciador de WiFi

Código 8 Função enviar para a API

/*

* Send data to API
* This process message and sends a ‘GET’ request to Google Sheets API

* @params Measure Pirani, MFC 1 , MFC 2, MFC 3, MFC 4
*/

void sendData(float Pirani_ESP, float MFC1_ESP, float MFC2_ESP, float

MFC3_ESP, float MFC4_ESP) {

//Processing data and sending data

String string_Pirani_ESP = | String(Pirani_ESP);
String string_MFC1_ESP = | String(MFC1_ESP);
String string_MFC2_ESP = | String(MFC2_ESP);
String string_MFC3_ESP = | String(MFC3_ESP);
String string_MFC4_ESP = | String(MFC4_ESP);

// prepare header to API

String url = "/macros/s/" + GAS_ID + "/exec?Pirani=" + string_Pirani_ESP

+ "&MFC1=" + string_MFC1_ESP+ "&MFC2=" + string_MFC2_ESP + "&MFC3=" +

string_MFC3_ESP + "&MFC4=" + string_MFC4_ESP;

//API GET

client.print(String("GET ") + url + " HTTP/1.1\r\n" +

"Host: " + host + "\r\n" +

"User-Agent: BuildFailureDetectorESP8266\r\n" +

"Connection: close\r\n\r\n");

}

4.3 Software

O software é responsável pela telemetria do equipamento. O banco de dados

NoSQL Firebase e o armazenamento no Google Sheets foram avaliados. O Firebase

é o mais indicado devido à velocidade de processamento e disponibilidade. Porém,

como a ideia do projeto é ser um protótipo funcional e minimizar custos, foi utilizado o

Google Sheets como repositório devido a sua gratuidade e a possibilidade de enviar

um maior número de mensagens do que a versão gratuita do Firebase.

Assim, através de uma planilha no Google Sheets (Figura 59), é possível gerar

uma API no Google Apps Script (Figura 60) para processar as mensagens que são

enviadas através de um url. O código 9 de processamento é escrito na linguagem

JavaScript.

Figura 59 Panilha recebendo dados do ESP01

Figura 60 Apps Scripts

Código 9 Google Sheets API

/**

* Function doGet: Parse received data from GET request,

get and store data which is corresponding with header row in Google

Spreadsheet
*/

function doGet(e) {
Logger.log( JSON.stringify(e) ); // view parameters

var result = 'Ok'; // assume success

if (e.parameter == 'undefined') {

result = 'No Parameters';

}

else {
var sheet_id = “****chave apagada****”; | // Spreadsheet ID
var sheet = SpreadsheetApp.openById(sheet_id).getActiveSheet(); | //

get Active sheet

var newRow = sheet.getLastRow() + 1;

var rowData = [];

d=new Date();

for (var param in e.parameter) {

Logger.log('In for loop, param=' + param); var value = stripQuotes(e.parameter[param]);

Logger.log(param + ':' + e.parameter[param]);

switch (param) {
case 'Pirani': //Parameter

rowData[0] = Utilities.formatDate(d, 'America/Sao_Paulo', 'yyyy-

MM-dd HH:mm:ss'); | // Timestamp in column A

rowData[1] = value; //Value in column B

result = 'Written on column B';

break;
case 'MFC1': //Parameter

rowData[3] = Utilities.formatDate(d, 'America/Sao_Paulo', 'yyyy-

MM-dd HH:mm:ss'); | // Timestamp in column A

rowData[4] = value; //Value in column C

result += ' ,Written on column C';

break;
case 'MFC2': //Parameter

rowData[6] = Utilities.formatDate(d, 'America/Sao_Paulo', 'yyyy-

MM-dd HH:mm:ss'); | // Timestamp in column A

rowData[7] = value; //Value in column C

result += ' ,Written on column D';

break;
case 'MFC3': //Parameter

rowData[9] = Utilities.formatDate(d, 'America/Sao_Paulo', 'yyyy-

MM-dd HH:mm:ss'); | // Timestamp in column A

rowData[10] = value; //Value in column C

result += ' ,Written on column E';

break;
case 'MFC4': //Parameter

rowData[12] = Utilities.formatDate(d, 'America/Sao_Paulo', 'yyyy-

MM-dd HH:mm:ss'); | // Timestamp in column A

rowData[13] = value; //Value in column C

result += ' ,Written on column F';

break;

default:

result = "unsupported parameter";

}

}

Logger.log(JSON.stringify(rowData));
// Write new row below

var newRange = sheet.getRange(newRow, 1, 1, rowData.length);

newRange.setValues([rowData]);

}
// Return result of operation

return ContentService.createTextOutput(result);

}
/**

* Remove leading and trailing single or double quotes */

function stripQuotes( value ) {
return value.replace(/^["']|['"]$/g, "");

}

O Grafana Cloud, camada gratuita, foi utilizado como servidor em nuvem para

conectar à planilha do Google Sheets com os dados de telemetria e transformar em

dashboards (Figura 61). Os dados são atualizados automaticamente a cada 6

segundos. As consultas são realizadas através de um conector através da API que

solicita os valores das colunas da planilha através de uma chave secreta que apenas

o usuário final tem acesso (Figura 62).

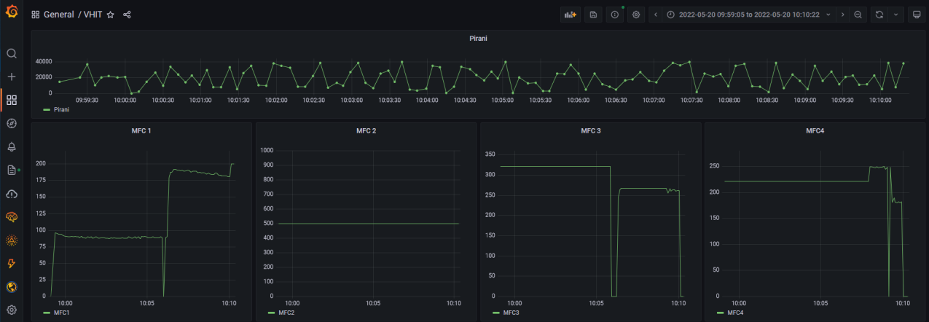
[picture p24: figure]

Figura 61 Dashboard no Grafana

Figura 62 Consulta planilha

Além disso, o Grafana permite criar outras funções durante a visualização

(soma, adição, derivadas etc.), alterar configurações dos gráficos (cor, texto, nome

das variáveis, unidades de medida etc.) e sendo possível utilizar mais de 20 modelos

de gráficos (Figura 63).

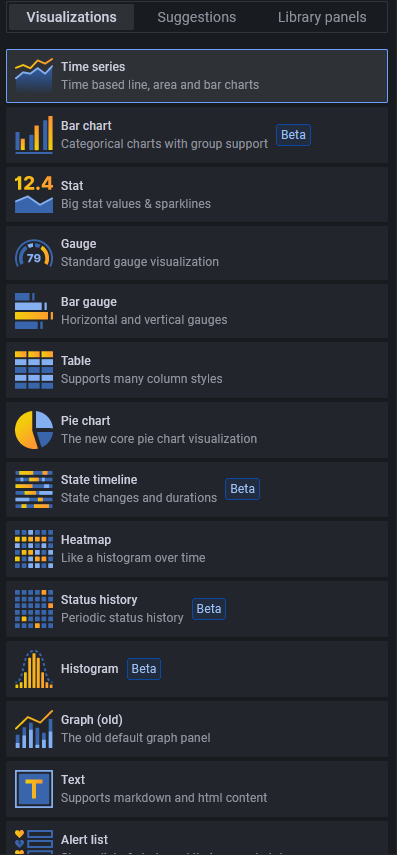
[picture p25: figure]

Figura 63 Modelos de gráfico

4.4 Testes do protótipo

Os testes realizados visaram certificar que o hardware, firmware e software

estão desempenhando suas funções e, assim, cumprindo os objetivos do projeto. O

Arduino Mega original utilizado queimou durante o desenvolvimento e para os testes

do protótipo final foi utilizado um Arduino Mega genérico o que pode ter ocasionado

em alterações no resultado.

Para o sensor Pirani, foi verificado o sinal gerado e comparado ao sinal de

referência do multímetro digital ICEL (2020) modelo MD-6111, calibração de fábrica,

em escala de 20 V e exatidão ±0,75%, representado como “exatidão” no manual

(Figura 64). O sinal de referência apresentado é a média dos valores medidos pelo

multímetro no período da medição. Além disso, foi avaliado sua repetibilidade

considerando: mesmo procedimento de medição, mesmo instrumento de medição,

mesmo local e repetição em um intervalo de 1 minuto (JCGM:100, 2008).

Para os controladores de fluxo de massa, foi comparado os valores de PWM

enviados ao MFC com os valores lidos no microcontrolador. Para o software, foi

enviado dados simulados pela porta serial do Arduino, já que não foi possível realizar

o teste no laboratório por conta do sinal de rede, roteado pelo celular, ser fraco. Além

disso, o ESP01 não está programado para conectarse à rede Wi-Fi por certificado

PEAP e MSCHAPv2, utilizado na rede disponibilizada pela UTFPR.

Figura 64 – Especificações multímetro para tensão contínua

Fonte: ICEL (2021)
Em todos os testes foi utilizado o gás hidrogênio fator de correção igual a

1.01- e controladores de fluxo de massa calibrados para nitrogênio que possui o fator

de correção igual 1-. O tempo de duração para cada teste foi variado aleatoriamente

para garantir que o protótipo atende diferentes valores.

Todos os testes foram realizados utilizando o protótipo final e com a presença

dos usuários do reator, assim, foi coletado e implementado os feedbacks da utilização

do protótipo.

4.4.1 Leitura da pressão

O teste da função de leitura do Pirani consistiu na medição da pressão no

reator do laboratório de tratamentos térmicos da UTFPR durante 50 segundos com

um fluxo constante de hidrogênio à 250 SCCM. Foi utilizado o sinal do multímetro

como referência (Figura 65).

Figura 65 – Preparação do laboratório para realização do teste

O resultado do teste pode ser visto na Figura 66. A curva azul é o resultado

gerado pelo protótipo através do arquivo CSV salvo no cartão microSD. A curva laranja

é o resultado encontrado se o fator de correção do gás for retirado.

Figura 66 Leitura da pressão no reator com fluxo constante de hidrogênio à 250 SCCM durante 50 segundos

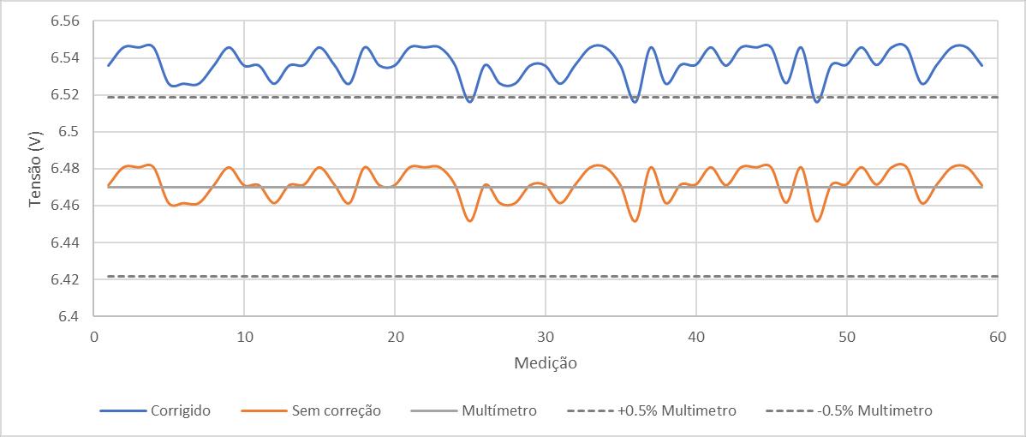
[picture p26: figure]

Como mencionado anteriormente, o teste foi repetido a fim de comprovar a

sua repetibilidade e que as variáveis no microcontrolador se reiniciaram corretamente.

O segundo teste tendo duração de 35 segundos (Figura 67).

Figura 67 – Leitura de pressão no reator com fluxo constante de hidrogenio à 250 SCCM

A precisão da medição da leitura do Pirani foi representada na Figura 68. O

cálculo se baseia no desvio padrão amostral das duas medições e desconsiderando

os valores corrigidos.

Figura 68 – Precisão da medição do Pirani

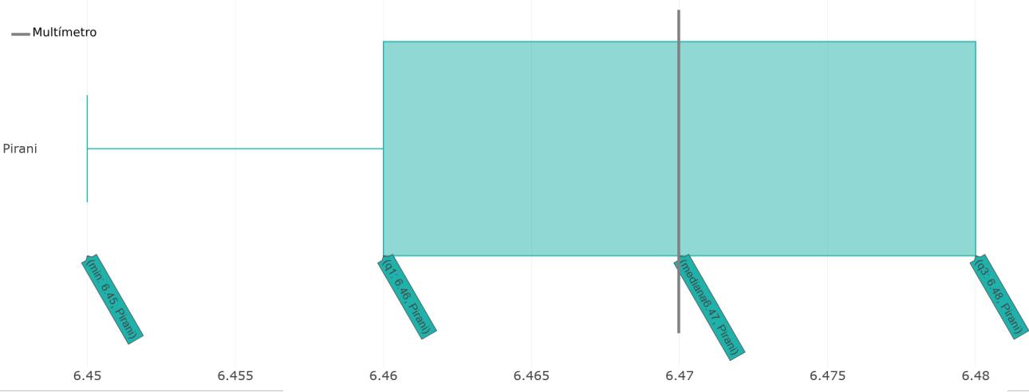
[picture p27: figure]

4.4.2 Leitura e controle do fluxo de massa

4.4.2.1Função continua

O teste da função contínua foi realizado durante 130 segundos. Foram

realizados 5 testes variando a abertura da válvula entre: 10,15, 50, 100, 250 e 500

SCCM (Figura 69 e 70). Segundo manual da MKS (2013), o MFC suporta um controle

de abertura dentre 2% a 100%, que é equivalente entre 10 SCCM a 500 SCCM.

Porém, o protótipo não conseguiu controlar o sensor com valores abaixo de 15 SCCM,

por isso, o teste para 10 SCCM foi interrompido antes do fim.

Figura 69 Função contínua variação de abertura de válvula

Figura 70 Resultados individuais da função contínua

4.4.2.2Função pulsada

O teste da função pulsada foi realizado durante 143 segundos com um pulso

de 13 segundos com válvula aberta e 13 segundos com a válvula fechada. Foi utilizado

um fluxo constante de hidrogênio à 250 SCCM (Figura 71).

Figura 69 Função pulsada 165 segundos

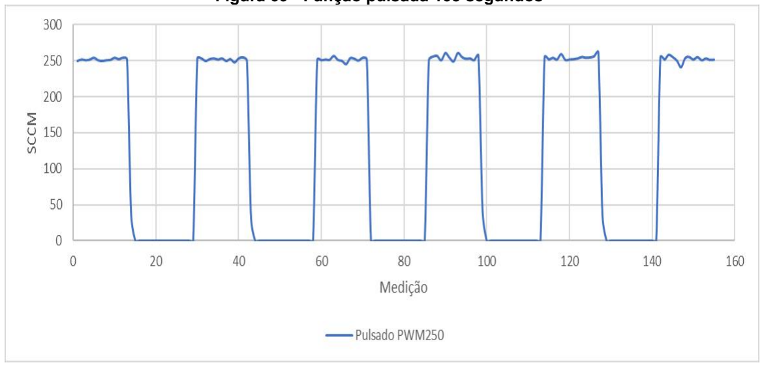
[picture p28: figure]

4.4.3 Módulo Wi-Fi

O teste do envio das medições via Wi-Fi foi realizado durante 300 segundos

utilizando a função contínua. Como foi mencionado anteriormente, os dados aleatórios

foram simulados através do software Nextion e enviados via porta serial do Arduino

(Figura 72). Porém não foi possível gerar os dados simulados do sensor Pirani. O

ESP01 limitase a enviar dados em um intervalo mínimo de 6 segundos (Quadro 8).

Figura 70 Dashboard Grafana

Quadro 8 Dados coletados pelo ESP01

4.4.4 Visão geral

A taxa de aquisição do protótipo foi calculada com equipamento variando o

número de MFC ligados simultaneamente (Figura 73). Há uma diminuição do tempo

de aquisição das medições pelo fato do Arduino não permitir as atividades simultâneas

(Multithreading), assim, as medições são sequênciais. Além disso, ainda é possível

otimizar a programação para aumentar a taxa de aquisição, porém a redução da taxa

por número de controladores ligados ainda permanecerá. Assim, a ordem de

prioridade de medição é crescente iniciando no MFC 1.

PIRANI | MFC1 | MFC2 | MFC3 | MFC4
Data e hora | medição | Data e hora | medição | Data e hora | medição | Data e hora | medição | Data e hora | medição
05/06/2022 22:36:52 | 0.01 | 05/06/2022 22:36:52 | 98.24 | 05/06/2022 22:36:52 | 180.35 | 05/06/2022 22:36:52 | 169.6 | 05/06/2022 22:36:52 | 174
05/06/2022 22:36:58 | 0.01 | 05/06/2022 22:36:58 | 98.24 | 05/06/2022 22:36:58 | 85.04 | 05/06/2022 22:36:58 | 137.34 | 05/06/2022 22:36:58 | 153.4
05/06/2022 22:37:03 | 0.01 | 05/06/2022 22:37:03 | 0 | 05/06/2022 22:37:03 | 76.74 | 05/06/2022 22:37:03 | 131.48 | 05/06/2022 22:37:03 | 148.09
05/06/2022 22:37:10 | 0.01 | 05/06/2022 22:37:10 | 0 | 05/06/2022 22:37:10 | 75.76 | 05/06/2022 22:37:10 | 131.96 | 05/06/2022 22:37:10 | 145.65
05/06/2022 22:37:17 | 0.01 | 05/06/2022 22:37:17 | 0 | 05/06/2022 22:37:17 | 76.25 | 05/06/2022 22:37:17 | 129.52 | 05/06/2022 22:37:17 | 145.16
05/06/2022 22:37:23 | 0.01 | 05/06/2022 22:37:23 | 0 | 05/06/2022 22:37:23 | 76.74 | 05/06/2022 22:37:23 | 131.48 | 05/06/2022 22:37:23 | 147.61
05/06/2022 22:37:29 | 0.01 | 05/06/2022 22:37:29 | 100.2 | 05/06/2022 22:37:29 | 175.95 | 05/06/2022 22:37:29 | 159.82 | 05/06/2022 22:37:29 | 150
05/06/2022 22:37:38 | 0.01 | 05/06/2022 22:37:38 | 100.68 | 05/06/2022 22:37:38 | 181.33 | 05/06/2022 22:37:38 | 164.22 | 05/06/2022 22:37:38 | 154
05/06/2022 22:37:44 | 0.01 | 05/06/2022 22:37:44 | 101.66 | 05/06/2022 22:37:44 | 181.33 | 05/06/2022 22:37:44 | 167.16 | 05/06/2022 22:37:44 | 155
05/06/2022 22:37:51 | 0.01 | 05/06/2022 22:37:51 | 101.17 | 05/06/2022 22:37:51 | 181.33 | 05/06/2022 22:37:51 | 167.16 | 05/06/2022 22:37:51 | 155
05/06/2022 22:37:57 | 0.01 | 05/06/2022 22:37:57 | 102.15 | 05/06/2022 22:37:57 | 181.82 | 05/06/2022 22:37:57 | 167.16 | 05/06/2022 22:37:57 | 159
05/06/2022 22:38:03 | 0.01 | 05/06/2022 22:38:03 | 102.15 | 05/06/2022 22:38:03 | 183.28 | 05/06/2022 22:38:03 | 169.11 | 05/06/2022 22:38:03 | 158
05/06/2022 22:38:09 | 0.01 | 05/06/2022 22:38:09 | 102.15 | 05/06/2022 22:38:09 | 181.82 | 05/06/2022 22:38:09 | 168.13 | 05/06/2022 22:38:09 | 158
05/06/2022 22:38:16 | 0.01 | 05/06/2022 22:38:16 | 101.66 | 05/06/2022 22:38:16 | 182.8 | 05/06/2022 22:38:16 | 166.67 | 05/06/2022 22:38:16 | 156
05/06/2022 22:38:22 | 0.01 | 05/06/2022 22:38:22 | 102.64 | 05/06/2022 22:38:22 | 183.77 | 05/06/2022 22:38:22 | 166.18 | 05/06/2022 22:38:22 | 159
05/06/2022 22:38:28 | 0.01 | 05/06/2022 22:38:28 | 102.64 | 05/06/2022 22:38:28 | 182.31 | 05/06/2022 22:38:28 | 166.67 | 05/06/2022 22:38:28 | 159
05/06/2022 22:38:34 | 0.01 | 05/06/2022 22:38:34 | 102.15 | 05/06/2022 22:38:34 | 182.31 | 05/06/2022 22:38:34 | 166.67 | 05/06/2022 22:38:34 | 157
05/06/2022 22:38:41 | 0.01 | 05/06/2022 22:38:41 | 102.64 | 05/06/2022 22:38:41 | 182.31 | 05/06/2022 22:38:41 | 166.18 | 05/06/2022 22:38:41 | 159
05/06/2022 22:38:47 | 0.01 | 05/06/2022 22:38:47 | 103.13 | 05/06/2022 22:38:47 | 182.31 | 05/06/2022 22:38:47 | 167.64 | 05/06/2022 22:38:47 | 156
05/06/2022 22:38:53 | 0.01 | 05/06/2022 22:38:53 | 103.62 | 05/06/2022 22:38:53 | 182.8 | 05/06/2022 22:38:53 | 167.16 | 05/06/2022 22:38:53 | 159
05/06/2022 22:38:59 | 0.01 | 05/06/2022 22:38:59 | 103.13 | 05/06/2022 22:38:59 | 182.8 | 05/06/2022 22:38:59 | 166.18 | 05/06/2022 22:38:59 | 159
05/06/2022 22:39:07 | 0.01 | 05/06/2022 22:39:07 | 102.64 | 05/06/2022 22:39:07 | 183.77 | 05/06/2022 22:39:07 | 168.13 | 05/06/2022 22:39:07 | 158
05/06/2022 22:39:13 | 0.01 | 05/06/2022 22:39:13 | 104.11 | 05/06/2022 22:39:13 | 182.8 | 05/06/2022 22:39:13 | 167.16 | 05/06/2022 22:39:13 | 157
05/06/2022 22:39:18 | 0.01 | 05/06/2022 22:39:18 | 103.13 | 05/06/2022 22:39:18 | 182.31 | 05/06/2022 22:39:18 | 167.16 | 05/06/2022 22:39:18 | 159
05/06/2022 22:39:25 | 0.01 | 05/06/2022 22:39:25 | 102.64 | 05/06/2022 22:39:25 | 183.28 | 05/06/2022 22:39:25 | 168.13 | 05/06/2022 22:39:25 | 159
05/06/2022 22:39:31 | 0.01 | 05/06/2022 22:39:31 | 103.13 | 05/06/2022 22:39:31 | 183.77 | 05/06/2022 22:39:31 | 166.67 | 05/06/2022 22:39:31 | 156
05/06/2022 22:39:37 | 0.01 | 05/06/2022 22:39:37 | 103.13 | 05/06/2022 22:39:37 | 182.8 | 05/06/2022 22:39:37 | 167.64 | 05/06/2022 22:39:37 | 158
05/06/2022 22:39:43 | 0.01 | 05/06/2022 22:39:43 | 104.11 | 05/06/2022 22:39:43 | 182.31 | 05/06/2022 22:39:43 | 169.6 | 05/06/2022 22:39:43 | 155
05/06/2022 22:39:50 | 0.01 | 05/06/2022 22:39:50 | 102.64 | 05/06/2022 22:39:50 | 183.28 | 05/06/2022 22:39:50 | 166.18 | 05/06/2022 22:39:50 | 159
05/06/2022 22:39:56 | 0.01 | 05/06/2022 22:39:56 | 103.13 | 05/06/2022 22:39:56 | 183.28 | 05/06/2022 22:39:56 | 165.69 | 05/06/2022 22:39:56 | 159
05/06/2022 22:40:02 | 0.01 | 05/06/2022 22:40:02 | 103.13 | 05/06/2022 22:40:02 | 182.31 | 05/06/2022 22:40:02 | 166.67 | 05/06/2022 22:40:02 | 158
05/06/2022 22:40:08 | 0.01 | 05/06/2022 22:40:08 | 103.62 | 05/06/2022 22:40:08 | 182.8 | 05/06/2022 22:40:08 | 167.64 | 05/06/2022 22:40:08 | 159
05/06/2022 22:40:14 | 0.01 | 05/06/2022 22:40:14 | 106.55 | 05/06/2022 22:40:14 | 188.17 | 05/06/2022 22:40:14 | 165.69 | 05/06/2022 22:40:14 | 0
05/06/2022 22:40:19 | 0.01 | 05/06/2022 22:40:19 | 107.04 | 05/06/2022 22:40:19 | 187.19 | 05/06/2022 22:40:19 | 167.64 | 05/06/2022 22:40:19 | 0
05/06/2022 22:40:25 | 0.01 | 05/06/2022 22:40:25 | 107.04 | 05/06/2022 22:40:25 | 186.71 | 05/06/2022 22:40:25 | 167.64 | 05/06/2022 22:40:25 | 0
05/06/2022 22:40:32 | 0.01 | 05/06/2022 22:40:32 | 107.04 | 05/06/2022 22:40:32 | 187.19 | 05/06/2022 22:40:32 | 166.67 | 05/06/2022 22:40:32 | 0
05/06/2022 22:40:39 | 0.01 | 05/06/2022 22:40:39 | 107.53 | 05/06/2022 22:40:39 | 187.68 | 05/06/2022 22:40:39 | 168.13 | 05/06/2022 22:40:39 | 0
05/06/2022 22:40:44 | 0.01 | 05/06/2022 22:40:44 | 107.04 | 05/06/2022 22:40:44 | 188.66 | 05/06/2022 22:40:44 | 166.67 | 05/06/2022 22:40:44 | 0
05/06/2022 22:40:51 | 0.01 | 05/06/2022 22:40:51 | 107.04 | 05/06/2022 22:40:51 | 188.17 | 05/06/2022 22:40:51 | 166.67 | 05/06/2022 22:40:51 | 0
05/06/2022 22:40:57 | 0.01 | 05/06/2022 22:40:57 | 104.11 | 05/06/2022 22:40:57 | 186.71 | 05/06/2022 22:40:57 | 168.13 | 05/06/2022 22:40:57 | 0
05/06/2022 22:41:02 | 0.01 | 05/06/2022 22:41:02 | 107.04 | 05/06/2022 22:41:02 | 187.68 | 05/06/2022 22:41:02 | 167.16 | 05/06/2022 22:41:02 | 0
05/06/2022 22:41:11 | 0.01 | 05/06/2022 22:41:11 | 107.53 | 05/06/2022 22:41:11 | 186.22 | 05/06/2022 22:41:11 | 168.13 | 05/06/2022 22:41:11 | 0
05/06/2022 22:41:17 | 0.01 | 05/06/2022 22:41:17 | 107.04 | 05/06/2022 22:41:17 | 186.22 | 05/06/2022 22:41:17 | 168.13 | 05/06/2022 22:41:17 | 0
05/06/2022 22:41:23 | 0.01 | 05/06/2022 22:41:23 | 107.04 | 05/06/2022 22:41:23 | 186.71 | 05/06/2022 22:41:23 | 167.64 | 05/06/2022 22:41:23 | 0
05/06/2022 22:41:29 | 0.01 | 05/06/2022 22:41:29 | 106.55 | 05/06/2022 22:41:29 | 186.22 | 05/06/2022 22:41:29 | 165.2 | 05/06/2022 22:41:29 | 0
05/06/2022 22:41:36 | 0.01 | 05/06/2022 22:41:36 | 106.06 | 05/06/2022 22:41:36 | 187.19 | 05/06/2022 22:41:36 | 168.13 | 05/06/2022 22:41:36 | 0
05/06/2022 22:41:41 | 0.01 | 05/06/2022 22:41:41 | 106.55 | 05/06/2022 22:41:41 | 187.19 | 05/06/2022 22:41:41 | 163.73 | 05/06/2022 22:41:41 | 0
05/06/2022 22:41:48 | 0.01 | 05/06/2022 22:41:48 | 108.02 | 05/06/2022 22:41:48 | 186.71 | 05/06/2022 22:41:48 | 165.69 | 05/06/2022 22:41:48 | 0
05/06/2022 22:41:55 | 0.01 | 05/06/2022 22:41:55 | 107.04 | 05/06/2022 22:41:55 | 187.19 | 05/06/2022 22:41:55 | 169.6 | 05/06/2022 22:41:55 | 0
05/06/2022 22:42:02 | 0.01 | 05/06/2022 22:42:02 | 111.44 | 05/06/2022 22:42:02 | 0 | 05/06/2022 22:42:02 | 0 | 05/06/2022 22:42:02 | 0
05/06/2022 22:42:08 | 0.01 | 05/06/2022 22:42:08 | 110.95 | 05/06/2022 22:42:08 | 0 | 05/06/2022 22:42:08 | 0 | 05/06/2022 22:42:08 | 0
05/06/2022 22:42:14 | 0.01 | 05/06/2022 22:42:14 | 111.93 | 05/06/2022 22:42:14 | 0 | 05/06/2022 22:42:14 | 0 | 05/06/2022 22:42:14 | 0
05/06/2022 22:42:21 | 0.01 | 05/06/2022 22:42:21 | 111.44 | 05/06/2022 22:42:21 | 0 | 05/06/2022 22:42:21 | 0 | 05/06/2022 22:42:21 | 0
05/06/2022 22:42:26 | 0.01 | 05/06/2022 22:42:26 | 111.44 | 05/06/2022 22:42:26 | 0 | 05/06/2022 22:42:26 | 0 | 05/06/2022 22:42:26 | 0

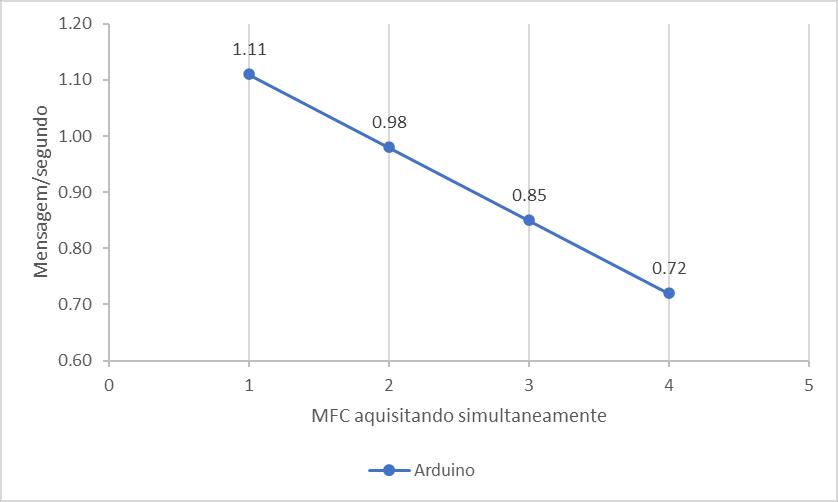
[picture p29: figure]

Figura 71 Taxa de aquisição x Número de MFC’s aquisitando

4.4.5 Custo do projeto

O Tabela 1 apresenta o custo do protótipo. O cálculo do orçamento não

considera os custos dos equipamentos como o sensor Pirani e o módulo de controle

de fluxo de massa. Além disso os valores de frete foram retirados de cada produto.

Tabela 1 Custo do projeto

O Quadro 9 apresenta o comparativo em uma visão geral das especificações

entre o protótipo e os produtos usados como referência.

Quadro 9 Comparação entre soluções

Componente | Unidade Preço/unidade
(R$) | Total
Arduino Mega | 1 | R$ | 200.00 R$ 200.00
Capacitor 1uF | 9 | R$ | 0.23 R$ 2.00
Case 3D | 1 | R$ | 45.00 R$ 45.00
Conector DB9 | 4 | R$ | 3.00 R$ 12.00
Conector RJ45 | 1 | R$ | 4.00 R$ 4.00
Conector Alimentação | 1 | R$ | 2.50 R$ 2.50
Fonte de alimentação 24V | 1 | R$ | 30.00 R$ 30.00
Modulo Leitor de microSD | 1 | R$ | 12.00 R$ 12.00
Modulo LM2596 StepDown | 1 | R$ | 15.00 R$ 15.00
Modulo WiFi ESP8266 | 1 | R$ | 20.00 R$ 20.00
PCB | 1 | R$ | 10.00 R$ 10.00
Resistor 4.7k Ohms | 6 | R$ | 0.05 R$ 0.30
Resistor 470 Ohms | 8 | R$ | 0.05 R$ 0.40
Resistor 220 Ohms | 1 | R$ | 0.05 R$ 0.05
RTC 1302 | 1 | R$ | 10.00 R$ 10.00
Tela Nextion 320x240 | 1 | R$ | 120.00 R$ 120.00
Transistor BC337 | 4 | R$ | 0.27 R$ 1.08
FRETE | | | R$ 60.00
TOTAL | | | R$ 544.33
Empresa | MKS Instruments | Brook Instrument | -
Modelo | 247 | 254 | v1.0
Dimensões (mm) | 240,5x274,3x88,1 | 211x113x58.8 | 165,5x74,6x41
Alimentação | 100 - 120 Vac | 12-24 Vdc ou 100 - 240 Vac | 24 Vdc
Material case | Aluminio | ABS Cycolac | PLA
Número de canais | 4 | 4 | 4 MFC e 1 Pirani
Tela | LED 1 linha x digito 3 1/2 0.56" | LCD 8 linhas x 40 digito | LCD 320x240 Sensível ao toque
Output de sinal | 0-5 volts | 0-5 volts | 0-5 volts
Compatibilidade | Modulo de controle massa (apenas MKS Intruments) | Modulo de controle pressao e massa (apenas Brook Intruments) | MFC: Quadro 4 Pirani: Quadro 6
Armazenamento de dados | Não armazena os dados | "100 anos de rentenção" | Cartão microSD até 64GB e 15GB em nuvem
Funções | Alimentação, leitura e controle de set point | Alimentação, leitura, controle de set point e armazenamento das medicoes | Alimentação, leitura, controle de set point, modo de operação e armazenamento das medicoes offline e online
Orçamento | R$ 21,395.00 | R$ 57,634.50 | R$ 545.00
Revendedor/data Orçamento | Ohmini 21/10/2021 | Contech 20/10/2021 | Autor 20/05/2022

Assim as funcionalidades do protótipo são:

- Ler e controlar até 4 controladores de fluxo de massa;
- Ler a pressão do sistema;
- Abertura de forma contínua da válvula durante período estipulado pelo

usuário;

- Abertura de forma pulsada da válvula durante período estipulado pelo

usuário;

- Correção da leitura da pressão e fluxo de massa de acordo com o gás

utilizado;

- Customizar o valor do fator de correção de gás;
- Customizar especificações técnicas de cada equipamento MFC (fluxo

máximo do equipamento e fator de gás calibrado);

- Gerar relatório online e offline das medições.

5 CONSIDERAÇÔES FINAIS

O protótipo cumpriu com a funcionalidade proposta e as necessidades para o

laboratório da UTFPR. Foi possível controlar simultaneamente os 4 MFC MKS 500

SCCM, ler as medições do sensor Pirani APGX-M-NW16/ALI Edward e ter todas as

medições salvas no microSD card. Os resultados da leitura do sensor Pirani se

mostraram mais precisos que as medições realizadas no multímetro, tendo σ=0,01.

Para o controle da válvula MFC, as funções contínua e pulsada cumpriram com os

objetivos apesar de apresentar picos no sinal durante o processo. Esses picos podem

ser solucionados através de um Arduino Mega original e alteração da resolução de

bits do sinal PWM. Além disso, é possível monitorar o tratamento térmico em um

período de 6 segundos entre medições através das plataformas do Google Sheet e

Grafana. A taxa de aquisição do protótipo (0,72 mensagens por segundo em carga

máxima de trabalho) ficou abaixo do esperado. Porém, essa taxa pode ser facilmente

corrigida com a otimização do código.

Assim, o resultado do protótipo mostra uma melhoria significativa no processo

de medição e controle dos sensores durante o tratamento térmico de matérias. O

sistema criado permite um maior controle do fluxo de gases no reator e aquisição dos

dados coletados.

Embora os resultados estejam aquém de uma solução comercial, é de se

destacar a inovação implementada deste projeto, visto que não foi encontrado

equipamento que permita diferentes modos de operação automatizados, conexão com

a internet, interface gráfica amigável, integração do sensor Pirani no equipamento e

preço acessível.

O desenvolvimento do projeto continuará mesmo após a entrega do trabalho

de conclusão do curso. A replicação do projeto do zero exige conhecimento técnico,

porém para diminuir essa barreira, foi desenvolvido um manual auxiliar os futuros

usuários que queiram contribuir no desenvolvimento do projeto (Apêndice E).

Como resultado acadêmico, este trabalho possibilitou o aprendizado e

aplicação de conhecimentos em diversas áreas tanto técnicas (sistema) quanto

sociais (analisar e entender as necessidades do usuário). Integrando conhecimentos

de engenharia mecânica, eletrônica e computação. Além disso, colaborando com o

desenvolvimento de pesquisas dentro do laboratório da UTFPR.

5.1 Trabalhos Futuros

Os resultados obtidos mostram que o sistema desenvolvido funciona

corretamente dentro do que foi proposto, assim, atendendo todos os requisitos do

projeto. Além disso, o protótipo poderia ter aprimoramentos:

- Utilização de um hardware com Wi-Fi embutido e com mais de um

núcleo, assim, permitindo multitarefas;

- Utilização de um processador de fácil integração na placa PCB;
- Otimização da programação;
- Garantir a não utilização de um hardware genérico;
- Utilização de um roteador de internet dentro do laboratório;
- Remodelar o case para montagem por encaixe clicáveis ao invés de

parafusos;

- Função para alteração de data e hora do RTC;

REFERÊNCIAS

ABDUL-QAWAY, A. The Internet of Things (IoT): An Overview. SUMAIT University, 2015.

AHMED, S. Modern Data Formats for Big Bioinformatics Data Analytics. International Journal of Advanced Computer Science and Applications, vol. 8, n. 4, 2017.

ALVES, C. Nitretação a plasma fundamentos e aplicações. v1, p. 6-16, 2001.

ARDUINO. Tech specs. Disponível em: < https://store.arduino.cc/products/arduino-mega-2560-rev3>. Acesso em: 02 de abril de 2022.

ARDUINO. | What | is | Arduino?. | Disponível | em:
<https://www.arduino.cc/en/Guide/Introduction/>. Acesso em: 30 de outubro de 2021.

AZOB. Knup fonte. Disponível em: < https://www.azob.com.br/none-37680710>. Acesso em: 05 de maio de 2022.

BISHOP, C. Vacuum Deposition onto Webs, Films and Foils. Computer Methods in Applied Mechanics and Engineering, v. 3, p. 62–63, 2015.

BROOKS INSTRUMENTS. Mass Flow Controllers & Meters. Disponível em: <https://www.brooksinstrument.com/en/products/massflowcontrollers>. Acesso em: 06 de outubro de 2021.

BRONKHORST. Thermal mass flow measurement working principle. Disponível em: <https://www.bronkhorst.com/int/servicesupport-1/technologies/thermalmass-flowmeasurement/>. Acesso em: 06 de outubro de 2021.

CARVALHO, P. Information Visualization for CSV Open Data Files Structure Analysis. University François Rabelais of Tours, Tours, França, 2015.

CHAO, L. Research on reliability design of data storage for Embedded System. School of Information Science and Technology, China, 2012.

CHOI, Y. Characteristic test methods of the thermal mass flow controller. Division of Physical Metrology, Korea Research Institute of Standards and Science, 2013.

DILLON, R. O. Thermochromic VO2 sputtered by control of a vanadiumoxygen emission ratio. Department of Electrical Engineering and Center for Microelectronic and Optical Materials Research University of Nebraska, 2001.

EDWARDS VACUUM. Active Gauges and Controllers. Disponível em: < https://www.edwardsvacuum.com/en/ourproducts/vacuummeasurement/active-gauges>. Acesso em: 06 de outubro de 2021.

EDWARDS VACUUM. Instructions manual – Linear Active Pirani Gauge. Estocolmo, Suécia, 2007.

EL-SABA. M. H. Fundamentals of Analog & Digital Signal Processing. Ain Shams University, 2015.

ESPRESSIF. | ESP32 | Series | | Datasheet | . | Disponível | em: | <
https://datasheet.lcsc.com/lcsc/1912261832_Espressif-Systems-ESP32-D0WD_C130167.pdf >. Acesso em: 01 de janeiro de 2022.
ESPRESSIF. | ESP8266 | Series | of | Modules. | Disponível | em: | <
https://www.espressif.com/en/products/socs/esp8266/>. Acesso em: 30 de outubro de 2021.
FLAT | UI | COLLORS. | UI | COLORS | PALLETE. | Disponível | em: | <
https://flatuicolors.com/palette/defo/>. Acesso em: 07 de abril de 2022.

GIT. Branching and Merging. Disponível em: <https://gitscm.com/about>. (https://git-scm.com/about) Acesso em: 01 de novembro de 2021.

HELMERSSON, U. Avaliação de dados de medição — Guia para a
expressão de incerteza de medição. BIPM, 2008. . Disponível em: <http://www.inmetro.gov.br/noticias/conteudo/iso_gum_versao_site.pdf>

JCGM 100. Ionized physical vapor deposition (IPVD): a review of technology and applications. Linküping University, 2008.

HORIBA. | What | is | a | Mass | Flow | Controller?. | Disponível | em: | <
https://www.horiba.com/en_en/fluidmeasurementandcontrol/>. Acesso em: 11 de outubro de 2021.

HULTMAN, L. Handbook of Hard Coatings – Deposition Technologies, Properties and Applications. Ed. Bunshaw, p. 111, 2001.

ICEL. Manual de instruções do multímetro digital modelo MD-6111. Brasil, 2020.

KOKAJ, A. Fast fourier transform and a complimentary filterbased control of a robotic system. Vienna University of Technology, 2018.

KOUTROULIS, E. Development of a Microcontroller-Based, Photovoltaic Maximum Power Point Tracking Control System. IEEE transactions on power electronics, vol. 16, n 1, janeiro, 2001.

KOYANAGI, F. Do You Know About ESP32 ADC Adjustment? Disponível em: < https://www.instructables.com/Do-You-Know-About-ESP32-ADC-Adjustment>. Acesso em: 15 de Dezembro de 2021.

KUMAR, U. Signal denoising using Fourier Analysis in Python. Disponível em: <https://www.earthinversion.com/techniques/signaldenoisingusingfastfourier-transform//>. Acesso em: 30 de outubro de 2021.

LAMMERINK, T. S. Pirani pressure sensor with distributed temperature sensing. University of Twente, 2001

LAST MINUTE ENGINEERING. Interfacing Micro SD Card Module with Arduino.
Disponível | em: | <https://lastminuteengineers.com/arduinomicrosdcardmodule-
tutorial/>. Acesso em: 05 de maio de 2022.

MARTINI, I. Copper for particle accelerators: electron stimulated desorption and study of hydrogen content measurement by laser ablation (msc thesis). Scuola di ingegneria dei processi industriali, 2012.

MICROSOFT. | Relational | vs. | NoSQL | data. | Disponível | em:
<https://docs.microsoft.com/enus/dotnet/architecture/cloudnative/relationalvs-nosqldata/>. Acesso em: 31 de outubro de 2021.

MKS INSTRUMENTS. Gas Correction Factors for Thermalbased Mass Flow. Disponível em: < https://www.mks.com/n/gascorrectionfactorsforthermalbased-massflowcontrollers>. Acesso em: 06 de maio de 2022.

MKS INSTRUMENTS. MKS G-Series Digital Mass Flow Controllers Instruction Manual. Estados Unidos da América, Janeiro, 2013.

MKS INSTRUMENTS. Multigas, Multirange, Elastomersealed, 5 50,000 sccm Mass Flow Controllers. Disponível em: < https://www.mksinst.com/f/ge50amass-flowcontroller>. Acesso em: 06 de outubro de 2021.

MORAIS, José. ESP32 – Analisando e corrigindo o ADC interno. Disponível em: < https://www.embarcados.com.br/esp32-adcinterno>. Acesso em: 15 de Dezembro de 2021.

MUDHOLKAR, P. A Beginner's Guide to Git and GitHub. Thakur Institute of Management Studies, Career Development & Research, Mumbai, India, 2017.

NEXTION. What’s Nextion?. Disponível em: <https://nextion.tech/>. Acesso em: 05 de maio de 2022.

ORACLE. O Que É um Banco de Dados Relacional ?. Disponível em: <https://www.oracle.com/br/database/whatisarelationaldatabase/>. Acesso em: 31 de outubro de 2021.

PAARMANN, L. D. Design and Analysis of Analog Filters: a Signal Processing Perspective. Kluwer academic publishers, v. 1, p. 23–58, 2001.

PANDIYARAJ, K. Influence of nonthermal plasma forming gases on improvement of surface properties of lowdensity polyethylene (LDPE). Applied Surface Science, v 307, p 109-11915, 2014.

PEREIRA, M. Implementação de um Banco de Dados Orientado a Objetos a Partir de um Modelo Dimensional. Instituto Federal de Educação, Ciência e Tecnologia de Minas Gerais, 2009.

PINEDO, C. Nitretação por plasma de aços inoxidáveis. Heat Tech – Tecnologia em Tratamento Térmico e Engenharia de Superfície. Brasil, 2004.

PLECHAWSKA-WOJCIK, M. Implementação de um Banco de Dados Orientado a Objetos a Partir de um Modelo Dimensional. Lublin University of Technology, 2017.

POLLARD, T. Secondary Analysis of Electronic Health Records. MIT Critical Data,
v. 1, cap. 11, p. 101-113, 2016.

QAZIZADEH, A. On active suspension in rail vehicles. KTH Royal Institute of Technology, Stockholm, 2017.

SENS4. What is the working principle of the Pirani gauge?. Disponível em: < https://sens4.com/piraniworkingprinciple.html>. Acesso em: 06 de outubro de 2021.

SHENOI, B. A. Introduction to Digital Signal Processing and Filter Design. Department of Electrical Engineering, Wright State University, v. 1, p. 29-43, 2006.

SPEIDEL, J. Introduction to digital communications. Springer, v.2, p. 3–49, 2021.

TEXAS INTRUMENTS. What is the working principle of the Pirani gauge LM2596 SIMPLE SWITCHER® Power Converter 150-kHz 3-A Step-Down Voltage
Regulator. | Disponível | em: | <
https://www.ti.com/lit/ds/symlink/lm2596.pdf?ts=1653608885656&ref_url=https%253 A%252F%252Fwww.google.com%252F (https://www.ti.com/lit/ds/symlink/lm2596.pdf?ts=1653608885656) >. Acesso em: 05 de maio de 2022.

TISON, S. A. A critical evaluation of thermal mass flow meters. National Institute of Standards and Technology, 1996.

TOPALLI, E. S. Pirani Vacuum Gauges Using Siliconon-Glass and Dissolved-Wafer Processes for the Characterization of MEMS Vacuum Packaging. IEEE sensors journal, v 9, n. 3, 2009

USINA INFO. Arduino RTC DS1302 Projeto Verificando o Tempo. Disponível em: <https://www.usinainfo.com.br/blog/arduinortcds1302-projetoverificandoo-tempo/>. Acesso em: 05 de maio de 2022.

XI, Y. Improvement of corrosion and wear resistances of AISI 420 martensitic stainless steel using plasma nitriding at low temperature. Northwestern Polytechnical University, 2007.

WILMSHURST, T. H. Signal recovery from noise in electronic instrumentation. Department of Electronics and Computer Science, University of Southampton, v. 2, p. 9-24, 1990.

APÊNDICE A Circuito Eletrônico

APÊNDICE B Quadro de fator de correção de gases

Gas | GFC
NH3 | 0.73
Ar | 1.39
AsH3 | 0.67
BCl3 | 0.41
Br2 | 0.81
CO2 | 0.7
CO | 1
N2 | 1
CCl4 | 0.31
CF4 | 0.42
Cl2 | 0.86
CHClF2 | 0.46
C2ClF5 | 0.24
CClF3 | 0.38
C2N2 | 0.61
D2 | 1
CBr2F2 | 0.19
B2H6 | 0.44
CCl2F2 | 0.35
CHCl2F | 0.42
SiH2Cl2 | 0.4
C2Cl2F4 | 0.22
C2H2F2 | 0.43
F2 | 0.98
CHF3 | 0.5
CCl3F | 0.33
CBrF3 | 0.37
C2Cl2F3 | 0.2
C2F6 | 0.24
C4F8 | 0.164
He | 1.45
H2 | 1.01
HBr | 1
HCl | 1
HF | 1
C4H8 | 0.29
Kr | 1.543
CH4 | 0.72
CH3F | 0.56
MoF6 | 0.21
Ne | 1.46
NO | 0.99
NF3 | 0.48
N2O | 0.71
O2 | 0.993
C3F8 | 0.17
COCl2 | 0.44
C3H8 | 0.36
C3H6 | 0.41
SiH4 | 0.6
SiCl4 | 0.28
SiF4 | 0.35
SO2 | 0.69
SF6 | 0.26
SiHCl3 | 0.33
C2Cl3F3 | 0.2
WF6 | 0.25
xe | 1.32
C5H12 | 0.22
C2H6 | 0.5

APÊNDICE C Modelos 3D do case e arquivos da PCB

Os modelos 3D do case podem ser encontrados no repositório do Github do

autor:

https://github.com/LincolnG4/Flowand-Pressure-Controller/tree/main/Hardware/CAD

Os arquivos de desenvolvimento da PCB podem ser encontrados no

repositório do GitHub do autor:

https://github.com/LincolnG4/Flowand-Pressure-Controller/tree/main/Hardware/PCB%26Eletronic

APÊNDICE D Códigos Firmware e Software

Os códigos referentes ao firmware podem ser encontrados no repositório do

GitHub do autor:

https://github.com/LincolnG4/Flowand-Pressure-Controller/tree/main/project

Arduino:

https://github.com/LincolnG4/Flowand-Pressure-Controller/tree/main/project/Arduino

- Main.ino:

https://github.com/LincolnG4/Flowand-Pressure-Controller/blob/main/project/Arduino/main.ino

- Controler.h:

https://github.com/LincolnG4/Flowand-Pressure-Controller/blob/main/project/Arduino/lib/controler.h

- Mfc.h:

https://github.com/LincolnG4/Flowand-Pressure-Controller/blob/main/project/Arduino/lib/mfc.h

- Pirani.h:

https://github.com/LincolnG4/Flowand-Pressure-Controller/blob/main/project/Arduino/lib/pirani.h

- Sdcard.h:

https://github.com/LincolnG4/Flowand-Pressure-Controller/blob/main/project/Arduino/lib/sdcard.h

- Touch.h:

https://github.com/LincolnG4/Flowand-Pressure-Controller/blob/main/project/Arduino/lib/touch.h

- clock_conf.h:

https://github.com/LincolnG4/Flowand-Pressure-Controller/blob/main/project/Arduino/lib/config/clock_conf.h

- mcu_conf.h

https://github.com/LincolnG4/Flowand-Pressure-Controller/blob/main/project/Arduino/lib/config/mcu_conf.h

- mfc_conf.h

https://github.com/LincolnG4/Flowand-Pressure-Controller/blob/main/project/Arduino/lib/config/mfc_conf.h

- pirani_conf.h

https://github.com/LincolnG4/Flowand-Pressure-Controller/blob/main/project/Arduino/lib/config/pirani_conf.h

- sdcard_conf.h

https://github.com/LincolnG4/Flowand-Pressure-Controller/blob/main/project/Arduino/lib/config/sdcard_conf.h

- wifi_conf.h

https://github.com/LincolnG4/Flowand-Pressure-Controller/blob/main/project/Arduino/lib/config/wifi_conf.h

ESP01:
https://github.com/LincolnG4/Flowand-Pressure-Controller/blob/main/project/ESP01/esp01.ino

LCD:
https://github.com/LincolnG4/Flowand-Pressure-Controller/tree/main/project/LCD

APÊNDICE E Manual do usuário

O manual do usuário pode ser encontrado no repositório do GitHub do autor:

https://github.com/LincolnG4/Flowand-Pressure-Controller

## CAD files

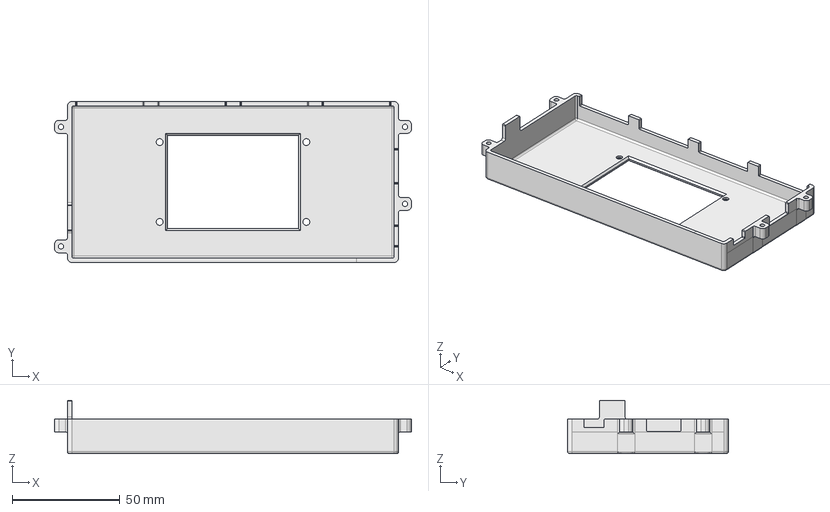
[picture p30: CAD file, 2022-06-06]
Hardware/CAD/case_top.FCStd
165.5 x 74.6 x 24.8 mm

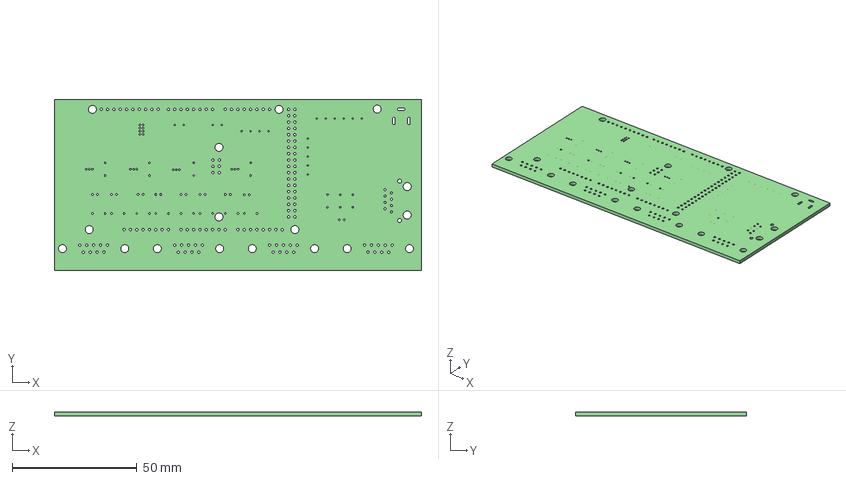
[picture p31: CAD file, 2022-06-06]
Hardware/PCB&Eletronic/TCC_Flow.step
147.3 x 68.6 x 1.60 mm

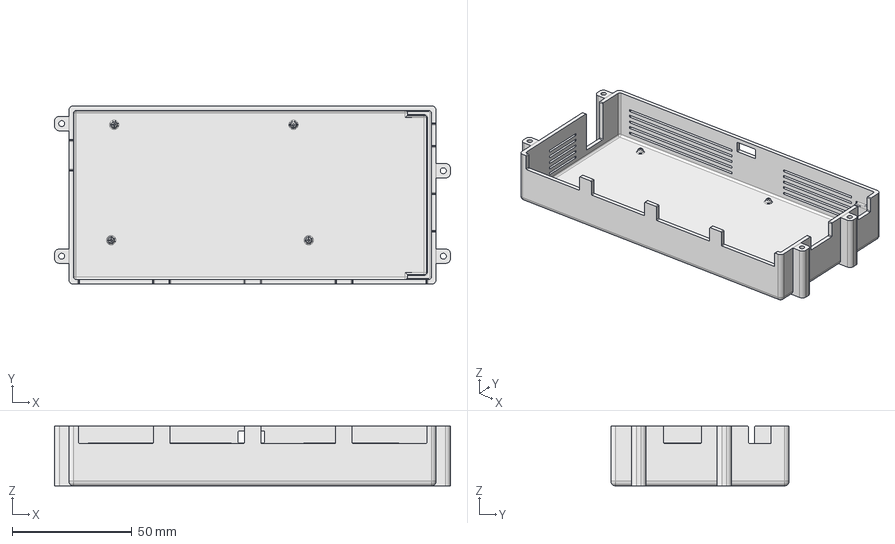
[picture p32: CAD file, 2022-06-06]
Hardware/CAD/case_bottom.FCStd
165.5 x 74.6 x 25.0 mm

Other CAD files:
Hardware/CAD/case_top-Body.stl

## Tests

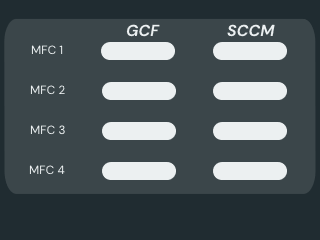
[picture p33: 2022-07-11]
project/LCD/teste/pag2.png

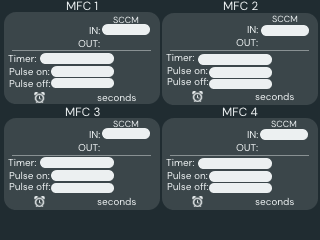
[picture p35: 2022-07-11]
project/LCD/teste/pag1.png

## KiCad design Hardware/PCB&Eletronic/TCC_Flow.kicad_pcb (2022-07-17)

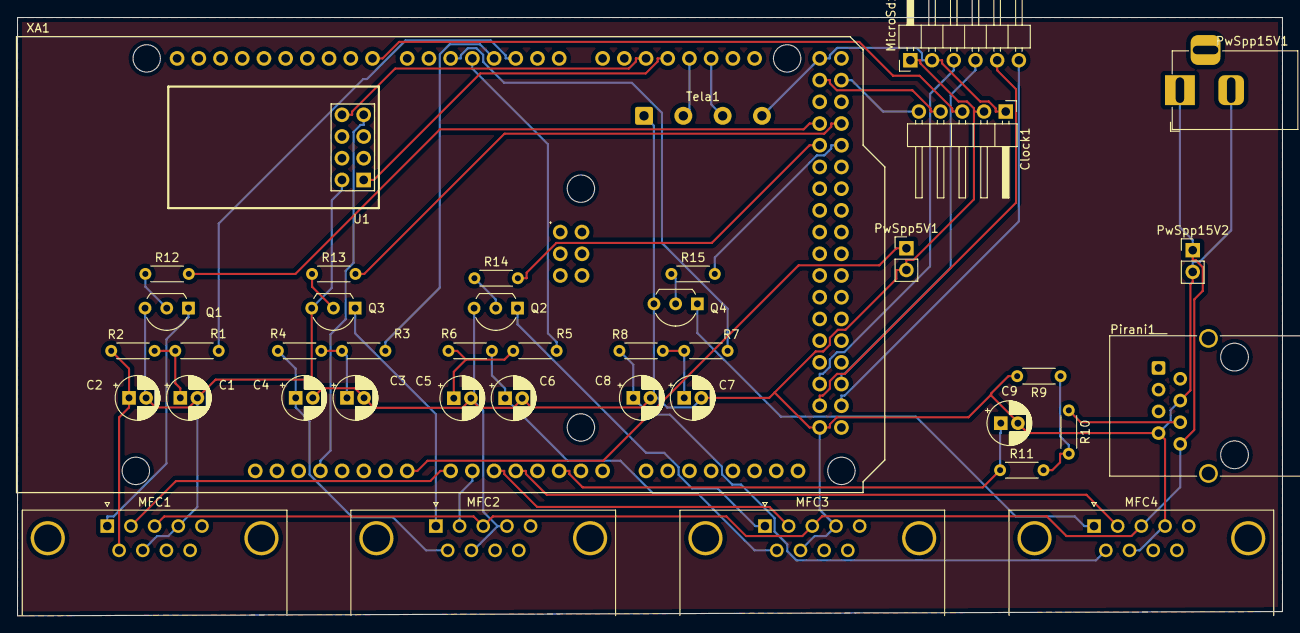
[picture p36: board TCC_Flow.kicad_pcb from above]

Board: 2 copper layers, 148.0 x 70.0 mm, 41 parts (0 on the bottom side), 47 nets.

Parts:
C1, C2, C3, C4, C5, C6, C7, C8, C9: 1uF; CP_Radial_D5.0mm_P2.00mm
Clock1: Conn_01x05_Male; PinHeader_1x05_P2.54mm_Horizontal
MFC1, MFC2, MFC3, MFC4: Conn_01x09_Male; DSUB-9_Male_Horizontal_P2.77x2.84mm_EdgePinOffset7.70mm_Hou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
MicroSd1: Conn_01x06_Male; PinHeader_1x06_P2.54mm_Horizontal
Pirani1: Conn_01x08_Male; RJ45_Wuerth_7499010001A_Horizontal
PwSpp5V1, PwSpp15V2: Conn_01x02_Male; PinHeader_1x02_P2.54mm_Vertical
PwSpp15V1: Conn_01x02_Male; BarrelJack_Horizontal
Q1, Q2, Q3, Q4: BC337; TO-92L_Inline_Wide
R1, R2, R3, R4, R5, R6, R7, R8: 500; R_Axial_DIN0204_L3.6mm_D1.6mm_P5.08mm_Horizontal
R9, R10: 4.6K; R_Axial_DIN0204_L3.6mm_D1.6mm_P5.08mm_Horizontal
R11: 220; R_Axial_DIN0204_L3.6mm_D1.6mm_P5.08mm_Horizontal
R12, R13, R14, R15: 4.7K; R_Axial_DIN0204_L3.6mm_D1.6mm_P5.08mm_Horizontal
Tela1: Conn_01x04_Male; SolderWire-0.5sqmm_1x04_P4.6mm_D0.9mm_OD2.1mm
U1: ESP-01v090; ESP-01
XA1: Arduino_Mega2560_Shield

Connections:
unnamed: C1.1, R1.1, R2.2
unnamed: C1.2, C2.2, C3.2, C4.2, C5.2, C6.2, C7.2, C8.2, C9.2, Clock1.2, MFC1.4, MFC1.7, MFC2.4, MFC2.7, MFC3.4, MFC3.7, MFC4.4, MFC4.7, MicroSd1.1, Pirani1.4, Pirani1.7, PwSpp5V1.2, PwSpp15V1.2, PwSpp15V2.2, Q1.3 (E), Q2.3 (E), Q3.3 (E), Q4.3 (E), R9.2, Tela1.1, U1.2 (GND), XA1.GND5 (GND)
unnamed: C2.1, MFC1.6, R2.1
unnamed: C3.1, R3.1, R4.2
unnamed: C4.1, MFC2.6, R4.1
unnamed: C5.1, R5.1, R6.2
unnamed: C6.1, MFC3.6, R6.1
unnamed: C7.1, R7.1, R8.2
unnamed: C8.1, MFC4.6, R8.1
unnamed: C9.1, R11.1, XA1.A5
unnamed: Clock1.1, MicroSd1.2, Tela1.4, XA1.5V3 (5V)
unnamed: Clock1.3, XA1.D8
unnamed: Clock1.4, XA1.D22
unnamed: Clock1.5, XA1.D23
unnamed: MFC1.1, Q1.1 (C)
unnamed: MFC1.2, XA1.A0
unnamed: MFC1.3, MFC2.3, MFC3.3, MFC4.3, Pirani1.8, PwSpp15V1.1, PwSpp15V2.1
unnamed: MFC2.1, Q3.1 (C)
unnamed: MFC2.2, XA1.A1
unnamed: MFC3.1, Q2.1 (C)
unnamed: MFC3.2, XA1.A2
unnamed: MFC4.1, Q4.1 (C)
unnamed: MFC4.2, XA1.A3
unnamed: MicroSd1.3, XA1.D50
unnamed: MicroSd1.4, XA1.D51
unnamed: MicroSd1.5, XA1.D52
unnamed: MicroSd1.6, XA1.D53 (D53_SS)
unnamed: Pirani1.6, R10.1
unnamed: PwSpp5V1.1, XA1.VIN
unnamed: Q1.2 (B), R12.1
unnamed: Q2.2 (B), R14.1
unnamed: Q3.2 (B), R13.1
unnamed: Q4.2 (B), R15.1
unnamed: R1.2, XA1.D2 (D2_INT0)
unnamed: R3.2, XA1.D3 (D3_INT1)
unnamed: R5.2, XA1.D4
unnamed: R7.2, XA1.D5
unnamed: R9.1, R10.2, R11.2
unnamed: R12.2, XA1.D26
unnamed: R13.2, XA1.D27
unnamed: R14.2, XA1.D28
unnamed: R15.2, XA1.D29
unnamed: Tela1.2, XA1.D18 (D18_TX1)
unnamed: Tela1.3, XA1.D19 (D19_RX1)
unnamed: U1.1 (UTXD), XA1.D17 (D17_RX2)
unnamed: U1.7 (VCC), XA1.3V3 (3.3V)
unnamed: U1.8 (URXD), XA1.D16 (D16_TX2)

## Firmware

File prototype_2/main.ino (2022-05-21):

#include <SD.h>
#include <SPI.h>
#include <stdlib.h>


#include "Nextion.h"
#define ledPin 13


/////////////////////////////////////////////////////////////////
//////////////////// CONFIGURE - RTC ///////////////////////////
///////////////////////////////////////////////////////////////

#include <virtuabotixRTC.h>
#include "TimeLib.h"

#include <UnixTime.h>
UnixTime stamp(-3); 

// Creation of the Real Time Clock Object
#define Clk 8  // Pino Clk
#define Dat 22 // Pino Dat
#define Rst 23 // Pino Rst

tmElements_t my_time;  // time elements structure
time_t unix_timestamp; // a timestamp

virtuabotixRTC myRTC(Clk, Dat, Rst);

String TimeString;
String ESP_MESSAGE = "0,0,0,0,0"; //PIRANI,MFC1,MFC2,MFC3,MFC4

/////////////////////////////////////////////////////////////////
//////////////////// CONFIGURE - SDCARD ////////////////////////
///////////////////////////////////////////////////////////////

#define pinCS 53

File Pirani_CSV;
File MFC_CSV_1;
File MFC_CSV_2;
File MFC_CSV_3;
File MFC_CSV_4;


/////////////////////////////////////////////////////////////////
//////////////////// CONFIGURE - ESP01 /////////////////////////
///////////////////////////////////////////////////////////////


int ESP_ENABLE=0;
int ESP_TIMER=0;
int ESP_DELAY=4;

/////////////////////////////////////////////////////////////////
//////////////////// CONFIGURE - PIRANI ////////////////////////
///////////////////////////////////////////////////////////////

#define Read_Pirani A5

const float SinalMCU = 5;
const int bitsMCU = 1023.0000;
const int sinalPirani = 10; 

float Pirani_V = 0;
double Pirani_Torr = 0.000;
String piraniReadPrint;


/////////////////////////////////////////////////////////////////
//////////////////// CONFIGURE - MFC ///////////////////////////
///////////////////////////////////////////////////////////////



#define Close_MFC1 26
#define Close_MFC2 27
#define Close_MFC3 28
#define Close_MFC4 29

#define MFC A0
#define PWM_INPUT1 2
#define MFC2 A1
#define PWM_INPUT2 3
#define MFC3 A2
#define PWM_INPUT3 4
#define MFC4 A3
#define PWM_INPUT4 5

const int sinalMKS = 5; 
float MFC_V = 0;
char buff[10];
uint32_t number2 = 0;  // Create variable to store value of slider

int mcfOutput1 = 1 ;
int mcfOutput2 = 1 ;
int mcfOutput3 = 1 ;
int mcfOutput4 = 1 ;

float Calibrated_MFC_1 = 1;
float Calibrated_MFC_2 = 1;
float Calibrated_MFC_3 = 1;
float Calibrated_MFC_4 = 1;


/////////////////////////////////////////////////////////////////
//////////////////// CONFIGURE - NEXTION ///////////////////////
///////////////////////////////////////////////////////////////

long randNumber;
char buf[10];

int CurrentPage = 0;  // Create a variable to store which page is currently loaded

//NEXTION
NexPage p0 = NexPage(0,0,"page0");
NexPage p1 = NexPage(1,0,"page1");
NexPage p2 = NexPage(2,0,"page2");
NexButton p0_b1 = NexButton(0,1,"b1");
NexButton p0_b2 = NexButton(0,2,"b2");
NexButton p1_b2 = NexButton(2,6,"b2");
NexButton p2_b1 = NexButton(1,1,"b0");
NexButton p1_b0 = NexButton(2,44,"b0");
NexDSButton bt2 = NexDSButton(2, 1, "bt2");
NexDSButton bt3 = NexDSButton(2, 5, "bt3");
NexDSButton bt4 = NexDSButton(2, 12, "bt0");
NexDSButton bt5 = NexDSButton(2, 13, "bt1");
NexDSButton bt6 = NexDSButton(2, 2, "bt6");
NexDSButton bt7 = NexDSButton(2, 16, "bt7");
NexDSButton bt9 = NexDSButton(2, 14, "bt4");
NexDSButton bt10 = NexDSButton(2, 15, "bt5");
NexDSButton bt8 = NexDSButton(2, 39, "bt8");
NexText t1 = NexText(1, 2, "t0");
NexText t2 = NexText(1, 3, "t1");
NexText t3 = NexText(1, 4, "t2");
NexText t4 = NexText(1, 5, "t3");
NexText t8 = NexText(2, 7, "t0");
NexText t9 = NexText(3, 26, "t4");
NexText t10 = NexText(2, 34, "t25");
NexText t11 = NexText(2, 35, "t26");
NexText t12 = NexText(2, 36, "t27");
NexText t13 = NexText(2, 37, "t28");
NexText t14 = NexText(2, 38, "t29");
NexText t15 = NexText(2, 40, "t30");
NexText t16 = NexText(2, 41, "t31");
NexText t17 = NexText(2, 42, "t32");
NexText t18 = NexText(2, 43, "t33");
NexText t19 = NexText(2, 4, "t1");
NexText t20 = NexText(2, 10, "t2");
NexText t21 = NexText(2, 11, "t3");
NexNumber n0 = NexNumber(2, 17, "n0");
NexNumber n1 = NexNumber(2, 18, "n1");
NexNumber n2 = NexNumber(2, 23, "n5");
NexNumber n3 = NexNumber(2, 21, "n2");
NexNumber n4 = NexNumber(2, 30, "n13");
NexNumber n5 = NexNumber(2, 27, "n10");
NexNumber n6 = NexNumber(2, 22, "n8");
NexNumber n7 = NexNumber(2, 26, "n9");
NexNumber n8 = NexNumber(2, 19, "n3");
NexNumber n9 = NexNumber(2, 20, "n4");
NexNumber n10 = NexNumber(2, 24, "n6");
NexNumber n11 = NexNumber(2, 25, "n7");
NexNumber n12 = NexNumber(2, 31, "n14");
NexNumber n13 = NexNumber(2, 32, "n15");
NexNumber n14 = NexNumber(2, 28, "n11");
NexNumber n15 = NexNumber(2, 29, "n12");
NexCheckbox c0 = NexCheckbox(2,6,"c0");
NexCheckbox c1 = NexCheckbox(2,3,"c1"); 
NexCheckbox c2 = NexCheckbox(2,8,"c2");
NexCheckbox c3 = NexCheckbox(2,9,"c3");

NexVariable v0 = NexVariable(0,4,"va0");
uint32_t pageVar=0;


NexTouch *nex_listen_list[] = {
  &v0,&p0,&p1,&p2,&p0_b1,&p0_b2,&p1_b0,&p2_b1,&p1_b2,&t1,&t2,&t3,&t4,&t8,&t19,&t20,&t21,&bt2,&bt3,&bt4,&bt5,&bt6,&bt7,&bt9,&bt10,&bt8,&c0,&c1,&c2,&c3,&n0,&n3,&n6,&n8,&n9,&n10,&n11,&n12,&n13,&n14,&n15, NULL
};

uint32_t next, myInt = 0;
uint32_t dual_state; 
uint32_t dual_state2; 
int s;
uint32_t number = 0;
char temp[10] = {0};

uint32_t checkbox1=0;
int timer_enable = 0;
int timer_enable_pulse = 0;
uint32_t timerMFC1 = 0;
uint32_t timerMFC1_pulse = 0;
uint32_t timerMFC1_pulse_on = 0;
uint32_t timerMFC1_pulse_off = 0;
int delta=0;
int delta_pulse=0;
uint32_t MFC1_mode_linear;
uint32_t MFC1_mode_pulse;
int total1;
float cycle_on;


uint32_t checkbox2=0;
int timer_enable2 = 0;
int timer_enable_pulse2 = 0;
uint32_t timerMFC2 = 0;
uint32_t timerMFC2_pulse = 0;
uint32_t timerMFC2_pulse_on = 0;
uint32_t timerMFC2_pulse_off = 0;
int delta2=0;
int delta2_pulse=0;
uint32_t MFC2_mode_linear;
uint32_t MFC2_mode_pulse;
int total2;
float cycle2_on;

uint32_t checkbox3=0;
int timer_enable3 = 0;
int timer_enable_pulse3 = 0;
uint32_t timerMFC3 = 0;
uint32_t timerMFC3_pulse = 0;
uint32_t timerMFC3_pulse_on = 0;
uint32_t timerMFC3_pulse_off = 0;
int delta3=0;
int delta3_pulse=0;
uint32_t MFC3_mode_linear;
uint32_t MFC3_mode_pulse;
int total3;
float cycle3_on;

uint32_t checkbox4=0;
int timer_enable4 = 0;
int timer_enable_pulse4 = 0;
uint32_t timerMFC4 = 0;
uint32_t timerMFC4_pulse = 0;
uint32_t timerMFC4_pulse_on = 0;
uint32_t timerMFC4_pulse_off = 0;
int delta4=0;
int delta4_pulse=0;
uint32_t MFC4_mode_linear;
uint32_t MFC4_mode_pulse;
int total4;
float cycle4_on;


uint32_t numberu1;
uint32_t numberu2;
uint32_t numberu3;
uint32_t numberu4;


/////////////////////////////////////////////////////////////////
//////////////////// FUNCTIONS /////////////////////////////////
///////////////////////////////////////////////////////////////


void p0_b1_Press(void *ptr) {
  CurrentPage = 1;
  p2.show();
}

void p2_b1_Press(void *ptr) {
  CurrentPage = 0;
  p0.show();
}
void p0_b2_Press(void *ptr) {
  CurrentPage = 2;
  p1.show();
}
void p1_b0_Press(void *ptr) {
  CurrentPage = 0;
  p0.show();
}


char buffer[100] = {0};
char buffer2[100] = {0};
char buffer3[100] = {0};
char buffer4[100] = {0};


float PiraniRead(uint32_t checkbox1,uint32_t checkbox2,uint32_t checkbox3,uint32_t checkbox4,NexText t_gas1,NexText t_gas2,NexText t_gas3,NexText t_gas4,int mcfOutput1,int mcfOutput2,int mcfOutput3,int mcfOutput4){
  float totalFlow=0;
  float correctionFactor=1;
  char bufferText[10];
  char bufferText2[10];
  char bufferText3[10];
  char bufferText4[10];
  float gas_factor_1 = 1;
  float gas_factor_2 = 1;
  float gas_factor_3 = 1;
  float gas_factor_4 = 1;

  Pirani_V = (sinalPirani/SinalMCU)*((SinalMCU*(analogRead(Read_Pirani)))/bitsMCU); 
  

  if(checkbox1==0 && checkbox2==0 && checkbox3==0 && checkbox4==0){
      Pirani_Torr = 10000.00*(pow(10,(Pirani_V-6.125)));
      return Pirani_Torr;
  } 
  else{
    if(checkbox1==1){
      
      totalFlow = totalFlow + mcfOutput1;
    
      memset(bufferText, 10, sizeof(bufferText));
      t8.getText(bufferText, sizeof(bufferText));
      gas_factor_1 = atof(bufferText);
    }
    if(checkbox2==1){
      
      totalFlow = totalFlow + mcfOutput2;

      memset(bufferText2, 10, sizeof(bufferText2));
      t19.getText(bufferText2, sizeof(bufferText2));
      gas_factor_2 = atof(bufferText2);
    }
    if(checkbox3==1){
      
      totalFlow = totalFlow + mcfOutput3;
      
      memset(bufferText3, 10, sizeof(bufferText3));
      t20.getText(bufferText3, sizeof(bufferText3));
      gas_factor_3 = atof(bufferText3);
    }
    if(checkbox4==1){
      
      totalFlow = totalFlow + mcfOutput4;

      memset(bufferText4, 10, sizeof(bufferText4));
      t21.getText(bufferText4, sizeof(bufferText4));
      gas_factor_4 = atof(bufferText4);
    }
    
    correctionFactor = checkbox1*(mcfOutput1/totalFlow)*gas_factor_1 + checkbox2*(mcfOutput2/totalFlow)*gas_factor_2 + checkbox3*(mcfOutput3/totalFlow)*gas_factor_3+ checkbox4*(mcfOutput4/totalFlow)*gas_factor_4;
    Pirani_Torr = 10000.00*(pow(10,((Pirani_V*correctionFactor)-6.125)));
    return Pirani_Torr;
  }

  
} 

float MFCRead(int MFC,char* mfcOutputString,NexText t,NexText t_out, float Calibrated_MFC){
  float gas_factor_in;
  float output_MFC_factor;
  char bufferText[10];

  MFC_V = 100*(sinalMKS/SinalMCU)*((SinalMCU*(analogRead(MFC)))/bitsMCU); 
  
  memset(bufferText, 10, sizeof(bufferText));
  t_out.getText(bufferText, sizeof(bufferText));

  gas_factor_in = atof(bufferText);
  
  output_MFC_factor = float(MFC_V)*(gas_factor_in/Calibrated_MFC);

  dtostrf(output_MFC_factor, 1, 2, mfcOutputString); 
  //itoa(output_MFC_factor,mfcOutputString, 10);     
  t.setText(mfcOutputString);

  return output_MFC_factor;
}



void SendTextT4(float Pirani_V){
  dtostrf(Pirani_V, 4, 3, buff);
  t10.setText(buff);
}

void WriteSD(File myFile,String message){
  if (myFile) {
    //Serial.print("Writing to test.txt...");
    myFile.println(message);
    // close the file:
    myFile.close();
    //Serial.println("done.");
  } else {
    // if the file didn't open, print an error:
    //Serial.println("error opening test.txt");
  }
}

float ReadCalibrate(NexText t_calibrate){
    float Text_Number;
    char bufferCalibrate[10];

    memset(bufferCalibrate, 10, sizeof(bufferCalibrate));
    t_calibrate.getText(bufferCalibrate, sizeof(bufferCalibrate));

    Text_Number = atof(bufferCalibrate);
    return Text_Number;
}

int MFCsetvalve(NexNumber n,uint32_t number){
  int val = number;

  n.getValue(&number);
  val = map(val, 0, 500, 0, 255);

  return val;
}
  
  
void MfcPwmON(int PWM_INPUT,int delta,char* buffer,NexText t,int val){

  analogWrite(PWM_INPUT, val);
  
  itoa(delta,buffer, 10);
  t.setText(buffer);
}

void MfcPwmOFF(int PWM_INPUT,NexCheckbox c){
  analogWrite(PWM_INPUT, 0);
  c.setValue(0);
}
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

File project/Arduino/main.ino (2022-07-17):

/*
*  Import libs with functions of each arduino module 
*  From folder ./lib import each lib
*/

#include "./lib/controler.h"

/*
* Function to get the values from Settings (page 2) 
* @param t_calibrate MFC SCCM value
* @return new float MFC SCCM calibration 
*/
float ReadCalibrate(NexText t_calibrate){

    float Text_Number;
    char bufferCalibrate[10];
    
    // memset is a memory allocation, change it if you need more bytes of memory
    memset(bufferCalibrate, 10, sizeof(bufferCalibrate));
    t_calibrate.getText(bufferCalibrate, sizeof(bufferCalibrate));  // get value from the LCD

    Text_Number = atof(bufferCalibrate); // convert Str->Float
    return Text_Number;
}


void setup() {
  
  Serial2.begin(115200); // Serial to control Display
  Serial1.begin(115200); // Serial to send data to ESP32

  /*
  * @SERIAL DEBUGGING
  * Enable serial debugging when you need to easily find errors in firmware
  * 1. Use 'Find&Replace' tool to uncomment/comment all debugging message
  * 1.1 Find    ---> //Serial.
  * 1.2 Replace ---> Serial.
  * 2. Upload to the hardware
  * 3. Open the serial monitor with USB connected
  * !!You must use debug serial only for debbunging purposes! It can affect the code's performance!!
  */
 
  // SERIAL DEBUGGING
  Serial.begin(115200);

  //Serial.println("[INFO] - Debug serial started");
  if (Serial1.available() > 0) {
    //Serial.println("[INFO]- Display serial started");
  }
  else{
    //Serial.println("[ERROR]- Display serial NOT started");
  }
  if (Serial2.available() > 0) {
    //Serial.println("[INFO] - ESP32 serial started");
  }
  else{
    //Serial.println("[ERROR]- ESP32 serial NOT started");
  }

  // Starts PWM pin - MFC valve control 
  pinMode(PWM_INPUT1, OUTPUT);
  pinMode(PWM_INPUT2, OUTPUT);
  pinMode(PWM_INPUT3, OUTPUT);
  pinMode(PWM_INPUT4, OUTPUT);

  // Set all PWM's pin to 'zero'
  analogWrite(PWM_INPUT1, 0);
  analogWrite(PWM_INPUT2, 0);
  analogWrite(PWM_INPUT3, 0);
  analogWrite(PWM_INPUT4, 0);

  // Starts transistor's pin - MFC close valve control     
  pinMode(Close_MFC1, OUTPUT);
  pinMode(Close_MFC2, OUTPUT);
  pinMode(Close_MFC3, OUTPUT);
  pinMode(Close_MFC4, OUTPUT);

  // Set all transistor's pin to HIGH = it closes MFC valve  
  digitalWrite(Close_MFC1, HIGH);
  digitalWrite(Close_MFC2, HIGH);
  digitalWrite(Close_MFC3, HIGH);
  digitalWrite(Close_MFC4, HIGH);


  pinMode(pinCS, OUTPUT); // Starts SDcard module pin
  
  pinMode(ledPin,OUTPUT); // Inbuilt LED to debugging 
  digitalWrite(ledPin, LOW);
  
  // Press event for LCD button 
  // p --> page
  // b --> button
  p1_b0.attachPop(p1_b0_Press, &p1_b0);
  p2_b1.attachPop(p2_b1_Press, &p2_b1); 
  p0_b1.attachPop(p0_b1_Press, &p0_b1); 
  p0_b2.attachPop(p0_b2_Press, &p0_b2); 

  // SD Card Initialization
  if (SD.begin())
  {
    //Serial.println("[INFO] - SD card is ready to use.");
    boolean SD_Status= true;
  } else
  {
    //Serial.println("[ERROR] - SD card initialization failed");
    return;
  }

  //Serial.println("[INFO]- Setup is done!");

  //myRTC.setDS1302Time(18,20, 15,2, 11, 7, 2022);
}
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

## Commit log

2021-10-31 Flow_oçd.drawio
2022-05-21 Dev Updated
    [gasfactor.xlsx]
2022-06-06 hardware files
    [TCC_Flow-B_Cu.gbr, TCC_Flow-B_Mask.gbr, TCC_Flow-B_Silkscreen.gbr, TCC_Flow-Edge_Cuts.gbr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]
2022-07-17 [PCB] Add updated pcb and Doc
    [MFC1.CSV, PIRANI.CSV, TCC_Flow-B_Cu.gbr, TCC_Flow-B_Mask.gbr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]
